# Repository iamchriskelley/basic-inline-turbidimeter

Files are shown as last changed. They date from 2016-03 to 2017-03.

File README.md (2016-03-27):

#Basic Inline Turbidimeter
##Purpose  
The Basic Inline Turbidimeter is designed to measure turbidity in a body of water, automatically, for the lowest possible price.  

##Function  
_How does the device measure a parameter?_  
This device is a back-scatter [nephelometrer](https://en.wikipedia.org/wiki/Nephelometer). A pair of infrared light-emitting diodes (IR LED) are mounted on either side of a light-to-frequency sensor. Some portion of this emitted light is scattered by suspended sediment as it passes through a sample of water. This scattered light is detected by an IR-sensitive [photodiode](https://en.wikipedia.org/wiki/Photodiode) mounted at a right angle to the center of the IR LED's light beam. The intensity of light detected by the photodiode is referenced to a calibration curve stored in the device's memory to interpolate the corresponding turbidity value, measured in [nephelometric turbidity units (NTU)](http://or.water.usgs.gov/grapher/fnu.html).  

_How does the device record data?_  
This device contains an SD card slot for storing data.   

_How does the device display data?_  
This device is intended for standalone data logging and does not include a display.  

_What units does the device report in?_  
Like all AWQUA turbidimeters, this device reports readings in  [nephelometric turbidity units (NTU)](http://or.water.usgs.gov/grapher/fnu.html).  

_How does the device communicate data electronically?_  
This device does not possess data telemetry capabilities, however they may be added for additional cost. See the [Communications](https://github.com/AWQUA/Communication) repo for options. 

##Use Case  
_Where can the device be safely used?_  
This device can handle temperatures up to 70C, and is intended for field conditions. It is water proof to at least one foot.

##Power  
_How is the device powered?_  
This device uses 3.3V DC power, and requires less than 100mA of current, and uses an internal 3.7V lithium polymer battery.

_How much power does it use?_  
In automated testing, this device was capable of taking a measurement every 15 minutes for 29.5 days.

##Standard and Testing  
_How was the device tested?_  
This device has so far only been tested in the Open Source Water lab. The testing consisted of:
(1) immersing a prototype device in a water bath which contains a spin plate for bath mixing  
(2) adding small doses of a colloidal suspension to the water bath while relaying readings from the prototype via Bluetooth  every 10 seconds
(3) on every fourth dose of colloidal suspension, sampling the water bath with a commercial handheld turbidimeter  
(4) analyzing the fit between the commercial and prototype open-source turbidimeter

_How did it perform?_  
Test results may be found in the `testing` subdirectory in the file `basic-inline-turbidimeter_analysis.20151021.xlsx`. These data will be updated as further testing is conducted.

_What performance standards does the device meet?_  
We have not evaluated this device against existing standards for backscatter turbidimeters yet, nor have we yet developed a new standard.

##Construction  

###Bill of Materials
| Quantity  | Part Description | Example Price (each) |
| :-------------: | ------------- | :-------------: |
| 1 | ATMega328P-PU microprocessor  | [$2.90](http://www.electrodragon.com/product/atmega328-with-arduino-optiboot-uno/)|
| 1 | LMT86 temperature sensor  | [$1.00](http://www.mouser.com/ProductDetail/Texas-Instruments/LMT86LP/?qs=sGAEpiMZZMvfFCidbTccA1jyVRrxk5nB%252bTEjPRynSGM%3d)|
| 1 | TSL230BRD  | [$5.03](http://www.mouser.com/ProductDetail/ams/TSL230BRD-TR/?qs=sGAEpiMZZMu97qiQi8P%252buifvOPr%252b402N67DKHn09PFo%3d)|
| 1 | LP2985 3.3V Voltage regulator  | [$1.04](http://www.mouser.com/ProductDetail/Texas-Instruments/LP2985-33DBVT/?qs=paYhMW8qfivCywxvLCGbYQ%3D%3D)|
| 2 | 10uF aluminum electrolytic capacitors  | [$0.24](http://www.mouser.com/ProductDetail/Nichicon/ULD1J100MDD1TD/?qs=sGAEpiMZZMvwFf0viD3Y3c1N%2fF%2fpDmX12XlNW9X9Y3vZmYyMo5GpOw%3d%3d)|
| 2 | 22pF ceramic capacitors  | [$0.03](http://www.mouser.com/ProductDetail/Vishay-BC-Components/K220J10C0GF5UH5/?qs=sGAEpiMZZMsh%252b1woXyUXj9nJp%252b8gphztXIKBUu3gv%252bs%3d)|
| 5 | 100nF ceramic capacitors  | [$0.06](http://www.mouser.com/ProductDetail/Vishay-BC-Components/K104Z15Y5VE5TL2/?qs=sGAEpiMZZMsh%252b1woXyUXj5VNmf0jXPWIrWjnp1zAXac%3d)|
| 4 | 100 ohm resistors  | [$0.10](http://www.mouser.com/ProductDetail/KOA-Speer/MOS1-2CT52R101J/?qs=sGAEpiMZZMtlubZbdhIBICYVxaT5CDYBpEIIN%2f0BoAk%3d)|
| 1 | 220 ohm resistors  | [$0.10](http://www.mouser.com/ProductDetail/KOA-Speer/MOS1-2CT52R221J/?qs=sGAEpiMZZMtlubZbdhIBICYVxaT5CDYBStqm8FrIljg%3d)|
| 1 | 1K ohm resistors 1% tolerance | [$0.10](http://www.mouser.com/ProductDetail/Vishay-Beyschlag/MBB02070C1001FCT00/?qs=sGAEpiMZZMtlubZbdhIBIAA6NYEPHyksoxlYyK2s%252btM%3d)|
| 4 | 10K ohm resistors  | [$0.10](http://www.mouser.com/ProductDetail/Vishay-Beyschlag/MBA02040C1002FCT00/?qs=sGAEpiMZZMtlubZbdhIBIP7908E9uONJr6Tgqqo7oLA%3d)|
| 1 | IR LED  | [$0.47](http://www.mouser.com/ProductDetail/Kingbright/WP7113SF4C/?qs=sGAEpiMZZMvAL21a%2fDhxMro1KOf4QOs%252bCw5JRgjZK8o%3d)|
| 1 | Momentary contact button  | [$1.50](http://www.mouser.com/)|
| 1 | SPST power switch  | [$1.50](http://www.mouser.com/)|
| x | Header pins (0.1" spacing)  | [$1.50](http://www.mouser.com/)|
|||
||Total Cost:|$xx.xx|
###Circuit Board
####Schematic
picture alt Schematic of Basic Handheld Turbidimeter circuit board
####Layout
picture alt Layout of Basic Handheld Turbidimeter circuit board
###Assembly
[forthcoming]  
##FAQ and Troubleshooting  
###Online Resources

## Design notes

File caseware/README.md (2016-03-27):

#Caseware
The case for the `basic-inline-turbidimeter` is an injection-moded plastic case in two halves, manufactured by [SERPAC](http://www.serpac.com/). This case measures 2.27 x 3.63 x 1.51 inches and -- with the addition of a matching rubber seal between the two case halves -- is waterproof. Example pricing information below.

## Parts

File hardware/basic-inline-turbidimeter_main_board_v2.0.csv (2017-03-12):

Part | Value | Device | Package | Description | MF | MPN | OC_FARNELL | OC_NEWARK | PROD_ID
*RTC |  | DS3231M | DS3231M
C1 | 18p | CAP0603-CAP | 0603-CAP | Capacitor
C2 | 18p | CAP0603-CAP | 0603-CAP | Capacitor
C4 | 100n | CAP0603-CAP | 0603-CAP | Capacitor
C5 | 100n | CAP0603-CAP | 0603-CAP | Capacitor
C6 | 100n | CAP0603-CAP | 0603-CAP | Capacitor
C7 | 100n | CAP0603-CAP | 0603-CAP | Capacitor
C8 | 100n | CAP0603-CAP | 0603-CAP | Capacitor
C12 | 10uF | CAP0603-CAP | 0603-CAP | Capacitor
IC1 | MEGA8-AI | MEGA8-AI | TQFP32-08 | MICROCONTROLLER |  | ATMEGA8-16AU | 9171371 | 73M8863
JP1 |  | M02PTH | 1X02 | Standard 2-pin 0.1 header. Use with"
JP2 |  | M01PTH | 1X01 | Header 1
JP5 |  | M06SILK_FEMALE_PTH | 1X06 | Header 6 |  |  |  |  | CONN-08437
JP6 |  | M06SILK_FEMALE_PTH | 1X06 | Header 6 |  |  |  |  | CONN-08437
JP8 |  | M07 | 1X07 | Header 7
MICRO-SD | MICROSD-1010030368 | MICROSD-1010030368 | MICROSD-1010030368
PAD1 | WIREPADSMD5-2,5 | WIREPADSMD5-2,5 | 5-2,5 | Wire PAD connect wire on PCB
PAD2 | WIREPADSMD5-2,5 | WIREPADSMD5-2,5 | 5-2,5 | Wire PAD connect wire on PCB
PAD3 | WIREPADSMD5-2,5 | WIREPADSMD5-2,5 | 5-2,5 | Wire PAD connect wire on PCB
PAD4 | WIREPADSMD5-2,5 | WIREPADSMD5-2,5 | 5-2,5 | Wire PAD connect wire on PCB
R1 | 10k | RESISTOR0603 | 0603-RES | Resistor
R2 | 1k | RESISTOR0603 | 0603-RES | Resistor
U$4 | LMT86 | LMT86 | LMT86
Y1 |  | CRYSTAL5X3 | CRYSTAL-SMD-5X3 | Crystals

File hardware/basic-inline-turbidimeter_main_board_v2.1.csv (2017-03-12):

Part | Value | Device | Package | Description
BT |  | M04PTH | 1X04 | Header 4
C1 | 18p | CAP0603-CAP | 0603-CAP | Capacitor
C2 | 18p | CAP0603-CAP | 0603-CAP | Capacitor
C3 | 10uF | CAP0603-CAP | 0603-CAP | Capacitor
C4 | 100n | CAP0603-CAP | 0603-CAP | Capacitor
C5 | 100n | CAP0603-CAP | 0603-CAP | Capacitor
C6 | 100n | CAP0603-CAP | 0603-CAP | Capacitor
C7 | OPT | CAP0603-CAP | 0603-CAP | Capacitor
C8 | 100n | CAP0603-CAP | 0603-CAP | Capacitor
C9 | 100n | CAP0603-CAP | 0603-CAP | Capacitor
C10 | 100n | CAP0603-CAP | 0603-CAP | Capacitor
C11 | 100n | CAP0603-CAP | 0603-CAP | Capacitor
C12 | 100n | CAP0603-CAP | 0603-CAP | Capacitor
FRAME1 | FRAME-LETTER | FRAME-LETTER | CREATIVE_COMMONS | Schematic Frame
IC1 | MEGA8-AI | MEGA8-AI | TQFP32-08 | MICROCONTROLLER
IC2 | LM358 | LM358D | SO08 | OP AMP also LM158; LM258; LM2904
IND |  | M02PTH | 1X02 | Standard 2-pin 0.1 header. Use with"
ISP | AVR_SPI_PRG_6PTH | AVR_SPI_PRG_6PTH | 2X3 | AVR ISP 6 Pin
JP1 |  | M01PTH | 1X01 | Header 1
LED1 |  | LED5MM | LED5MM | LEDs
LED2 |  | LED5MM | LED5MM | LEDs
LED3 |  | LED5MM | LED5MM | LEDs
LED4 |  | LED5MM | LED5MM | LEDs
ND |  | M01PTH | 1X01 | Header 1
PW |  | M01PTH | 1X01 | Header 1
PWR |  | M03PTH | 1X03 | Header 3
R1 | 32k | RESISTOR0603 | 0603-RES | Resistor
R2 | 10k | RESISTOR0603 | 0603-RES | Resistor
R3 | 10k | RESISTOR0603 | 0603-RES | Resistor
R4 | 10k | RESISTOR0603 | 0603-RES | Resistor
R5 | 10k | RESISTOR0603 | 0603-RES | Resistor
R6 | 22 | RESISTOR0603 | 0603-RES | Resistor
R7 | 10k | RESISTOR0603 | 0603-RES | Resistor
R8 | OPT | RESISTOR0603 | 0603-RES | Resistor
R13 | 10k | RESISTOR0603 | 0603-RES | Resistor
R14 | 10k | RESISTOR0603 | 0603-RES | Resistor
R16 | 10k_<1% | RESISTOR0603-RES | 0603-RES | Resistor
RD |  | M01PTH | 1X01 | Header 1
REED |  | M02PTH | 1X02 | Standard 2-pin 0.1 header. Use with"
RT |  | M01PTH | 1X01 | Header 1
RTC |  | M04PTH | 1X04 | Header 4
SJ1 | JUMPER-PAD-2-NOYES_SILK | JUMPER-PAD-2-NOYES_SILK | PAD-JUMPER-2-NO_YES_SILK
SJ2 | JUMPER-PAD-2-NOYES_SILK | JUMPER-PAD-2-NOYES_SILK | PAD-JUMPER-2-NO_YES_SILK
T1 | 2N2222 | 2N2222 | TO92-EBC-OVAL | NPN TRANSISTOR
T2 | 2N2222 | 2N2222 | TO92-EBC-OVAL | NPN TRANSISTOR
THERM |  | RESISTOR0603-RES | 0603-RES | Resistor
TP |  | M01PTH | 1X01 | Header 1
TSL267 |  | M03PTH | 1X03 | Header 3
U1 | EEPROM-I2CSMD | EEPROM-I2CSMD | SO08 | I2C EEPROM chips, 24LC256 (and others)
U2 | EEPROM-I2CSMD | EEPROM-I2CSMD | SO08 | I2C EEPROM chips, 24LC256 (and others)
U3 | ADS1115 | ADS1115IDGST | SOP50P490X110-10N | Analog-to-Digital Converter with Internal Reference
U4 | MCP9808 | MCP9808-E/MS | SOP65P490X110-8N | Board Mount Temperature Sensors Silicon temp sensor with I2C interface
UART |  | M06SILK_FEMALE_PTH | 1X06 | Header 6
Y1 |  | CRYSTAL5X3 | CRYSTAL-SMD-5X3 | Crystals

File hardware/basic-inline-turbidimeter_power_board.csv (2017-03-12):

Part | Value | Device | Package | Description | PROD_ID
+OUT- |  | M02PTH | 1X02 | Standard 2-pin 0.1 header. Use with"
1UF |  | CAP0603-CAP | 0603-CAP | Capacitor
2.2UF |  | CAP0603-CAP | 0603-CAP | Capacitor
C3 | 4.7uF | CAP0402-CAP | 0402-CAP | Capacitor
C4 | 4.7uF | CAP0402-CAP | 0402-CAP | Capacitor
D1 | GREEN | LED0603 | LED-0603 | LEDs
D2 | MBRA140 | MBRA140 | SMA-DIODE | 40V, 1A Schottky rectifier | DIO-08053
D11 | RED | LED0603 | LED-0603 | LEDs
JMP |  | M02PTH | 1X02 | Header 2
JP2 |  | M02PTH | 1X02 | Standard 2-pin 0.1 header. Use with"
JP7 | LiPo Battery | M02-JST-2MM-SMT | JST-2-SMD | Header 2
OPT_10NF |  | CAP0603-CAP | 0603-CAP | Capacitor
R1 | R330 | RESISTOR0402-RES | 0402-RES | Resistor
R2K | 2K | RESISTOR0402-RES | 0402-RES | Resistor
R330 | 330 | RESISTOR0402-RES | 0402-RES | Resistor
U$2 | LP2985 | LP2985 | LP2985
U1 | MCP73831 | MCP73831 | SOT23-5 | Microchip's MCP73831

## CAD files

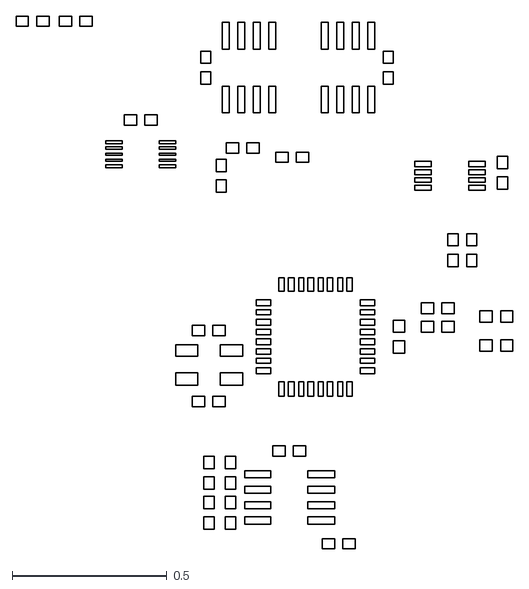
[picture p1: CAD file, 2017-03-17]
hardware/basic-inline-turbidimeter_main_board_v2.1.dxf
1.61 x 1.72

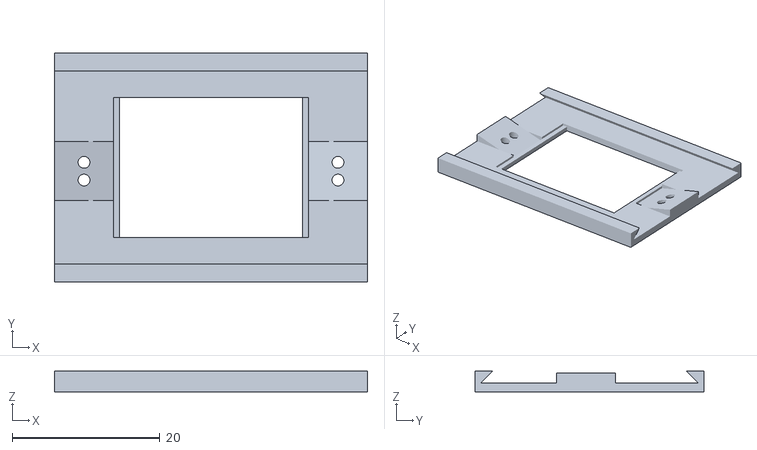
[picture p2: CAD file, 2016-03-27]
caseware/inline-light-angler.stl
42.4 x 31.0 x 2.80

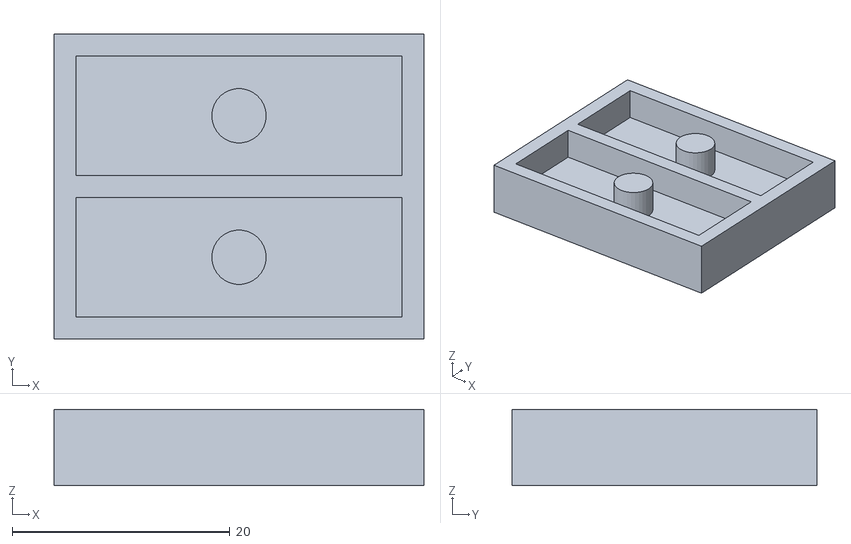
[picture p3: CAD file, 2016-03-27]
caseware/inline-cable-gaskets.stl
34.0 x 28.0 x 7.00

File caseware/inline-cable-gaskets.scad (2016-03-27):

$fn=30;
difference(){
    cube([34,28,7]);
    translate([2,2,3]) difference(){
        cube([30,11,4]);
        translate([15,5.5,0]) cylinder(r=2.5, h=4);
    }
    translate([2,15,3]) difference(){
        cube([30,11,4]);
        translate([15,5.5,0]) cylinder(r=2.5, h=4);
    }
}

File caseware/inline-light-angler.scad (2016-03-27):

$fn=30;

//translate([4,13,4]) rotate([0,-90,0]) 
light_shield();


module prism(hgt,sz){
rotate([0,0,0]) linear_extrude(height=hgt, center=true)
polygon(points = [ [0,0], [0,sz], [sz,sz]], paths = [ [0, 1, 2]]);
}

module light_shield(){
lightback();
translate([34.4,0,0]) rotate([0,0,180]) lightback();
translate([-4,10,0]) cube([42.4,6,1.2]);
translate([-4,-15,0]) cube([42.4,6,1.2]);
translate([-4,-15,0]) cube([42.4,6,1.2]);
translate([17.2,13.6,2.8]) rotate([0,90,0]) prism(42.4,2.4);
translate([17.2,-15,0.4]) rotate([90,0,90]) prism(42.4,2.4);
}

module lightback(){
    union(){
        difference(){
            //cylinder(r=4, h=2);
            translate([-4,-4,0]) cube([8,8,3]);
            //translate([-1,0,1.6]) rotate([0,15,0]) cylinder(r=10, h=3);
            translate([0,0,3]) rotate([0,15,0]) cube([18,18,3], true);
            translate([0,1.2,0])  cylinder(r=.8, h=3);
            translate([0,-1.2,0])  cylinder(r=.8, h=3);
        }
        translate([-4,4,0]) cube([8,6,1.2]);
        translate([-4,-10,0]) cube([8,6,1.2]);
        translate([4,-10,0]) cube([.8,20,.8]);
    }
}

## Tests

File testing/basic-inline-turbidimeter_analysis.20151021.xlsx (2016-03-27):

writing to logfile | 574 | 3.29 | 2015-10-21 16:07 | 1050.667
writing to logfile | 574.06 | 3.29 | 2015-10-21 16:07 | 1156.333
writing to logfile | 573.81 | 3.29 | 2015-10-21 16:07 | 1157.5
writing to logfile | 574 | 3.29 | 2015-10-21 16:08 | 1158.5
writing to logfile | 573.56 | 3.3 | 2015-10-21 16:08 | 1159.667
writing to logfile | 573.5 | 3.29 | 2015-10-21 16:08 | 1160.667
writing to logfile | 573.31 | 3.29 | 2015-10-21 16:08 | 1158
writing to logfile | 573.19 | 3.3 | 2015-10-21 16:08 | 1158
writing to logfile | 573.13 | 3.3 | 2015-10-21 16:08 | 1157.667
writing to logfile | 573.13 | 3.29 | 2015-10-21 16:09 | 1164
writing to logfile | 573.19 | 3.29 | 2015-10-21 16:09 | 1159
writing to logfile | 572.75 | 3.3 | 2015-10-21 16:09 | 1160.833
writing to logfile | 572.94 | 3.29 | 2015-10-21 16:09 | 1159
writing to logfile | 573.06 | 3.29 | 2015-10-21 16:09 | 1157.167
writing to logfile | 572.94 | 3.29 | 2015-10-21 16:09 | 713.667
writing to logfile | 572.81 | 3.3 | 2015-10-21 16:10 | 936.167
writing to logfile | 572.63 | 3.29 | 2015-10-21 16:10 | 911.667
writing to logfile | 572.63 | 3.29 | 2015-10-21 16:10 | 600.167
writing to logfile | 572.31 | 3.29 | 2015-10-21 16:10 | 204
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

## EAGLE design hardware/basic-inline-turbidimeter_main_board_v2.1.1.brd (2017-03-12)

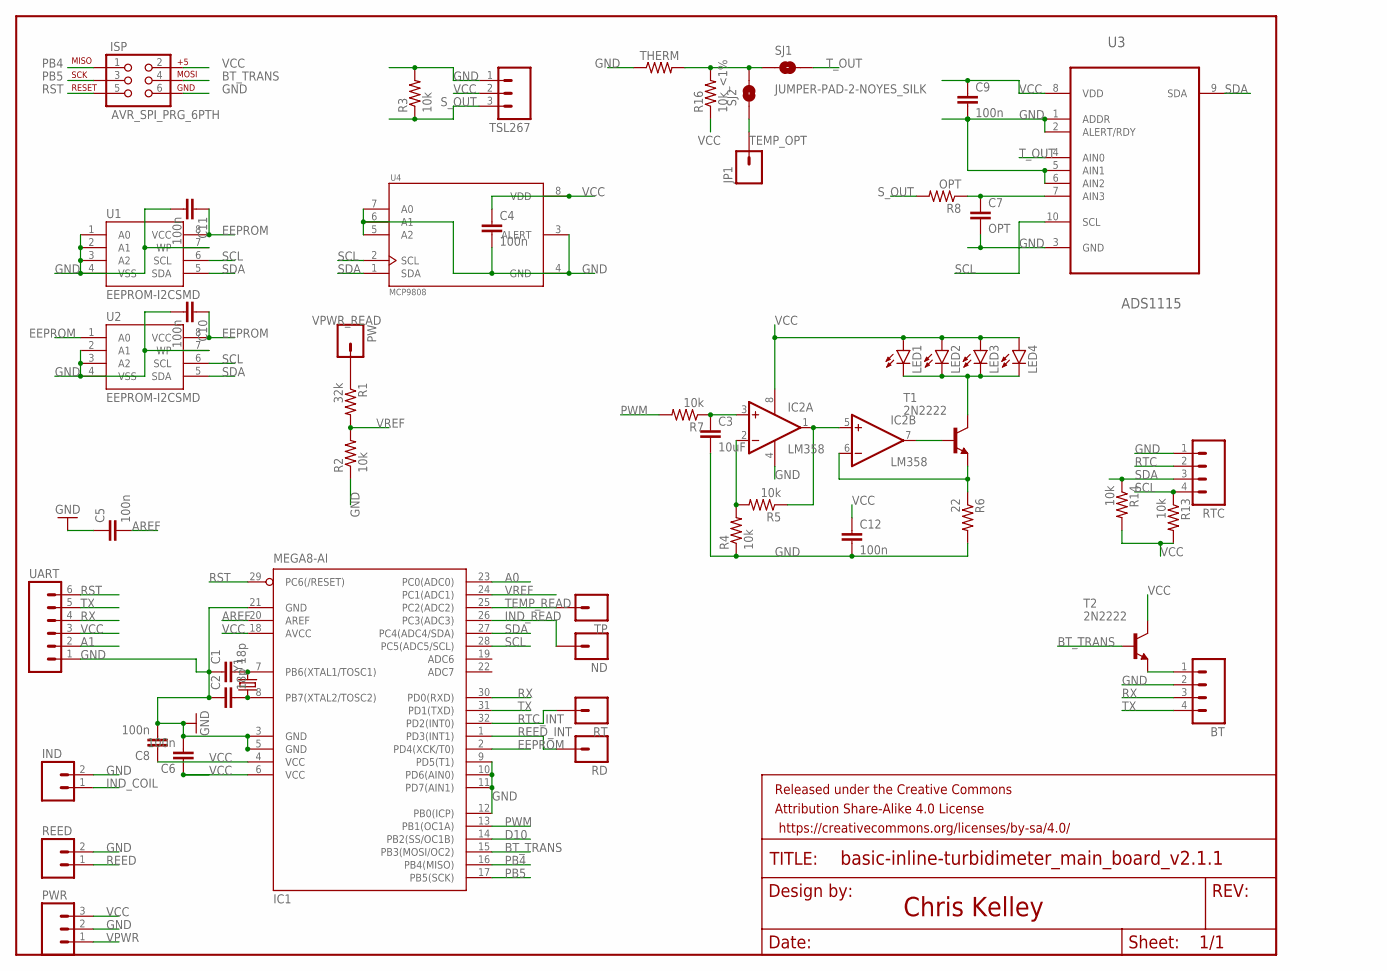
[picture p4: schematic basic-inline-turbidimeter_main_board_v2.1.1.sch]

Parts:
BT: M04PTH; 1X04
C1, C2: 18p; 0603-CAP
C3: 10uF; 0603-CAP
C4, C5, C6, C8, C9, C10, C11, C12: 100n; 0603-CAP
C7: OPT; 0603-CAP
FRAME1: FRAME-LETTER; CREATIVE_COMMONS
IC1: MEGA8-AI; TQFP32-08
IC2: LM358; SO08
IND: M02PTH; 1X02
ISP: AVR_SPI_PRG_6PTH; 2X3
JP1: M01PTH; 1X01
LED1, LED2, LED3, LED4: LED5MM
ND: M01PTH; 1X01
PW: M01PTH; 1X01
PWR: M03PTH; 1X03
R1: 32k; 0603-RES
R2, R3, R4, R5, R7, R13, R14: 10k; 0603-RES
R6: 22; 0603-RES
R8: OPT; 0603-RES
R16: 10k_<1%; 0603-RES
RD: M01PTH; 1X01
REED: M02PTH; 1X02
RT: M01PTH; 1X01
RTC: M04PTH; 1X04
SJ1, SJ2: JUMPER-PAD-2-NOYES_SILK; PAD-JUMPER-2-NO_YES_SILK
T1, T2: 2N2222; TO92-EBC-OVAL
THERM: RESISTOR0603-RES; 0603-RES
TP: M01PTH; 1X01
TSL267: M03PTH; 1X03
U1, U2: EEPROM-I2CSMD; SO08
U3: ADS1115; SOP50P490X110-10N
U4: MCP9808; SOP65P490X110-8N
UART: M06SILK_FEMALE_PTH; 1X06
Y1: CRYSTAL5X3; CRYSTAL-SMD-5X3

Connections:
A0: IC1.23 (PC0(ADC0))
A1: UART.2
AREF: C5.2, IC1.20 (AREF)
BT_TRANS: IC1.15 (PB3(MOSI/OC2)), ISP.4, T2.B
D10: IC1.14 (PB2(SS/OC1B))
EEPROM: C10.1, C11.1, IC1.2 (PD4(XCK/T0)), U1.8 (VCC), U2.1 (A0), U2.8 (VCC)
GND: BT.2, C1.1, C2.1, C3.2, C4.2, C5.1, C6.2, C7.2, C8.2, C9.2, C10.2, C11.2, C12.2, IC1.3 (GND), IC1.5 (GND), IC1.9 (PD5(T1)), IC1.10 (PD6(AIN0)), IC1.11 (PD7(AIN1)), IC1.12 (PB0(ICP)), IC1.21 (GND), IC2.4 (V-), IND.2, ISP.6, PWR.2, R2.1, R3.2, R4.1, R6.2, REED.2, RTC.1, THERM.1, TSL267.1, U1.1 (A0), U1.2 (A1), U1.3 (A2), U1.4 (VSS), U1.7 (WP), U2.2 (A1), U2.3 (A2), U2.4 (VSS), U2.7 (WP), U3.1 (ADDR), U3.2 (ALERT/RDY), U3.3 (GND), U3.5 (AIN1), U3.6 (AIN2), U4.3 (ALERT), U4.4 (GND), U4.5 (A2), U4.6 (A1), U4.7 (A0), UART.1
IND_COIL: IND.1
IND_READ: IC1.26 (PC3(ADC3)), ND.1
unnamed: LED1.K (C), LED2.K (C), LED3.K (C), LED4.K (C), T1.C
unnamed: C7.1, R8.1, U3.7 (AIN3)
unnamed: C3.1, IC2.3 (+IN), R7.1
unnamed: IC2.1 (OUT), IC2.5 (+IN), R5.1
unnamed: IC2.7 (OUT), T1.B
unnamed: IC2.2 (-IN), R4.2, R5.2
unnamed: IC2.6 (-IN), R6.1, T1.E
unnamed: BT.1, T2.E
unnamed: R16.2, SJ1.1, SJ2.2, THERM.2
PB4: IC1.16 (PB4(MISO)), ISP.1
PB5: IC1.17 (PB5(SCK)), ISP.3
PWM: IC1.13 (PB1(OC1A)), R7.2
Q1: C2.2, IC1.8 (PB7(XTAL2/TOSC2)), Y1.1
Q2: C1.2, IC1.7 (PB6(XTAL1/TOSC1)), Y1.3 (2)
REED: REED.1
REED_INT: IC1.1 (PD3(INT1)), RD.1
RST: IC1.29 (PC6(/RESET)), ISP.5, UART.6
RTC: RTC.2
RTC_INT: IC1.32 (PD2(INT0)), RT.1
RX: BT.3, IC1.30 (PD0(RXD)), UART.4
SCL: IC1.28 (PC5(ADC5/SCL)), R13.1, RTC.4, U1.6 (SCL), U2.6 (SCL), U3.10 (SCL), U4.2 (SCL)
SDA: IC1.27 (PC4(ADC4/SDA)), R14.1, RTC.3, U1.5 (SDA), U2.5 (SDA), U3.9 (SDA), U4.1 (SDA)
S_OUT: R3.1, R8.2, TSL267.3
TEMP_OPT: JP1.1, SJ2.1
TEMP_READ: IC1.25 (PC2(ADC2)), TP.1
TX: BT.4, IC1.31 (PD1(TXD)), UART.5
T_OUT: SJ1.2, U3.4 (AIN0)
VCC: C4.1, C6.1, C8.1, C9.1, C12.1, IC1.4 (VCC), IC1.6 (VCC), IC1.18 (AVCC), IC2.8 (V+), ISP.2, LED1.A, LED2.A, LED3.A, LED4.A, PWR.3, R13.2, R14.2, R16.1, T2.C, TSL267.2, U3.8 (VDD), U4.8 (VDD), UART.3
VPWR: PWR.1
VPWR_READ: PW.1, R1.1
VREF: IC1.24 (PC1(ADC1)), R1.2, R2.2

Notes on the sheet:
Chris Kelley

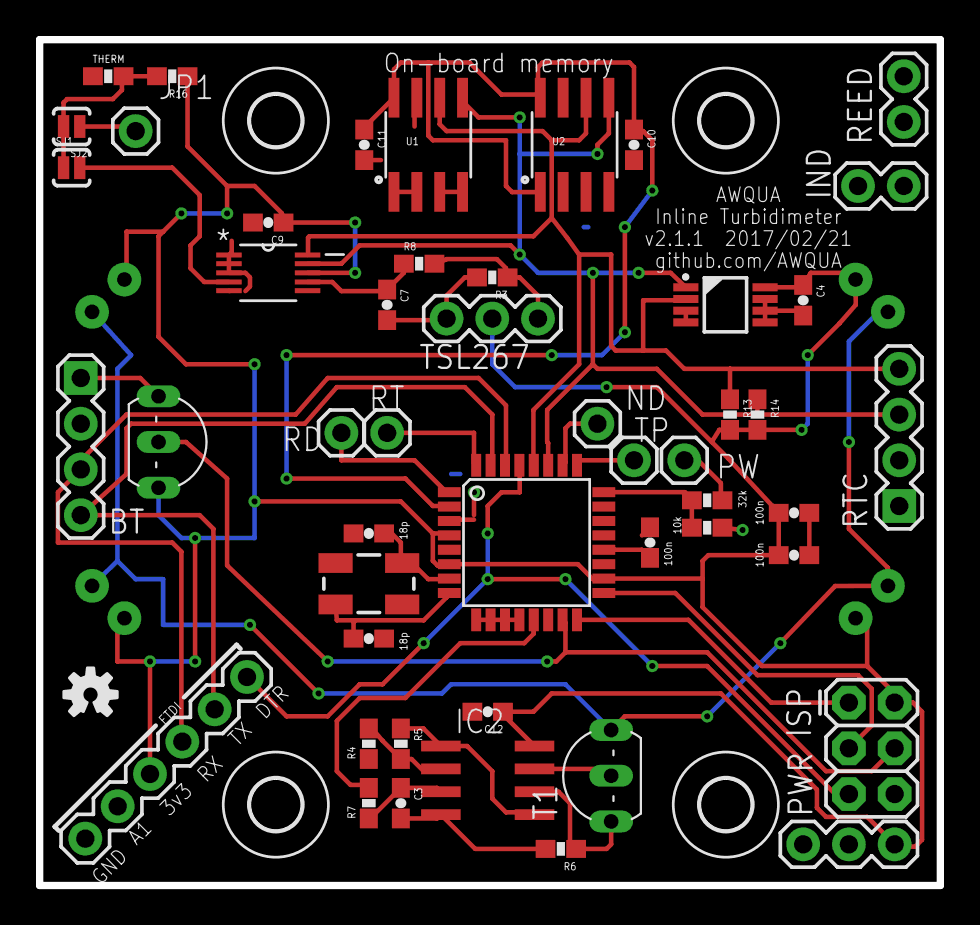
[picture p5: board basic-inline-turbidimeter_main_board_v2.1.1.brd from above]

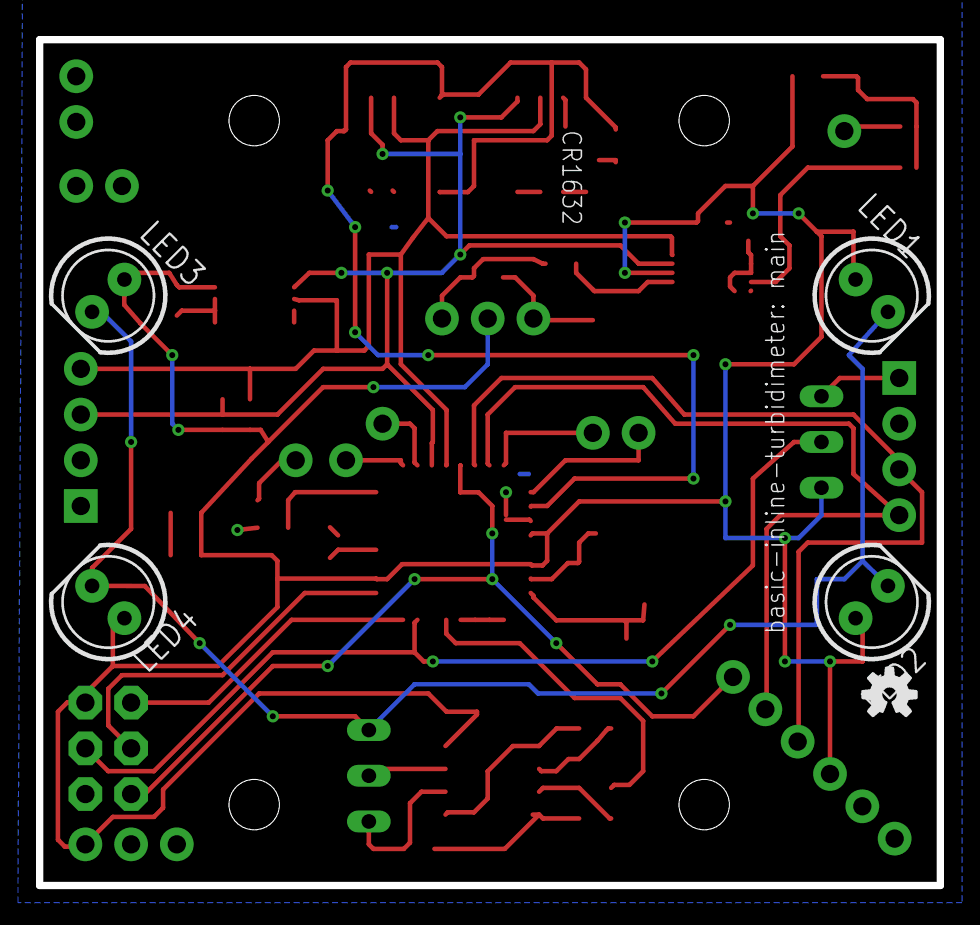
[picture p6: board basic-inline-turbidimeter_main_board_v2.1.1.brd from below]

Board: 2 copper layers, 50.0 x 47.0 mm, 60 parts (5 on the bottom side), 33 nets.

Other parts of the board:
U$1, U$3, U$5, U$6: 2,8
U$2, U$8: OSHW-LOGO-S

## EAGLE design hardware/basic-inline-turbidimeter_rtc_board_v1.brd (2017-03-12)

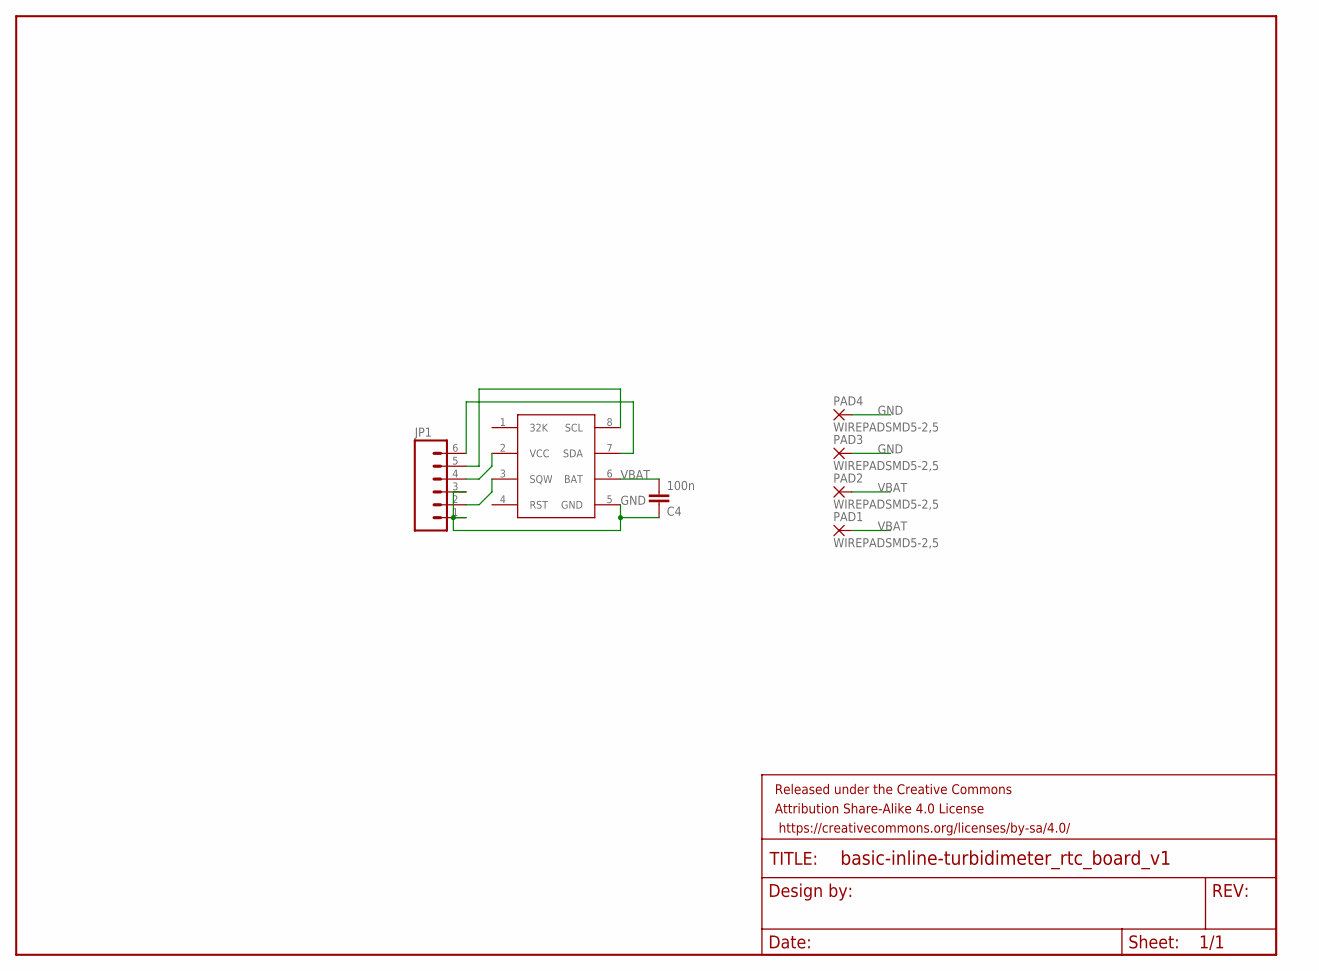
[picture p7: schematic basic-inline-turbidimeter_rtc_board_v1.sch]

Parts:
*RTC: DS3231M
C4: 100n; 0603-CAP
FRAME1: FRAME-LETTER; CREATIVE_COMMONS
JP1: M06SILK_FEMALE_PTH; 1X06
PAD1, PAD2, PAD3, PAD4: WIREPADSMD5-2,5; 5-2,5

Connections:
GND: *RTC.5 (GND), C4.1, JP1.1, JP1.3, PAD3.1, PAD4.1
unnamed: *RTC.3 (SQW), JP1.2
SCL: *RTC.8 (SCL), JP1.5
SDA: *RTC.7 (SDA), JP1.6
VBAT: *RTC.6 (BAT), C4.2, PAD1.1, PAD2.1
VCC: *RTC.2 (VCC), JP1.4

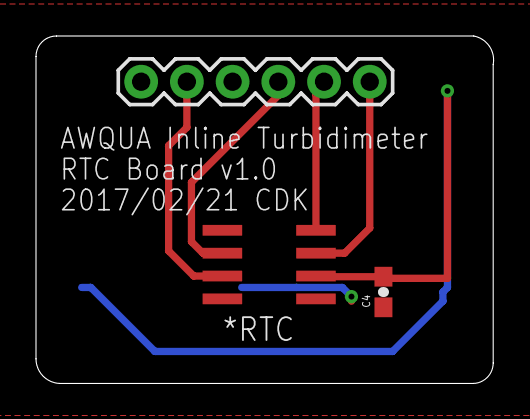
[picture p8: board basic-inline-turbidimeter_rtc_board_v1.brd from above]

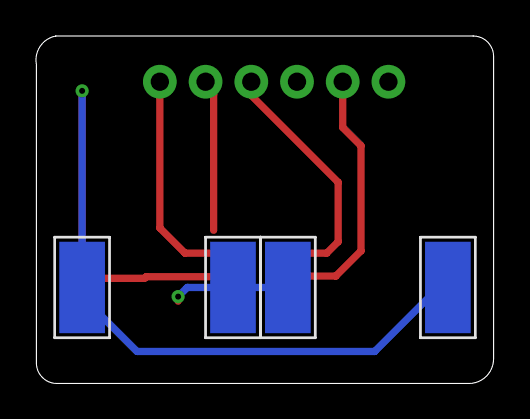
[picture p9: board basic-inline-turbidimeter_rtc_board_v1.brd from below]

Board: 2 copper layers, 25.4 x 19.3 mm, 8 parts (4 on the bottom side), 6 nets.

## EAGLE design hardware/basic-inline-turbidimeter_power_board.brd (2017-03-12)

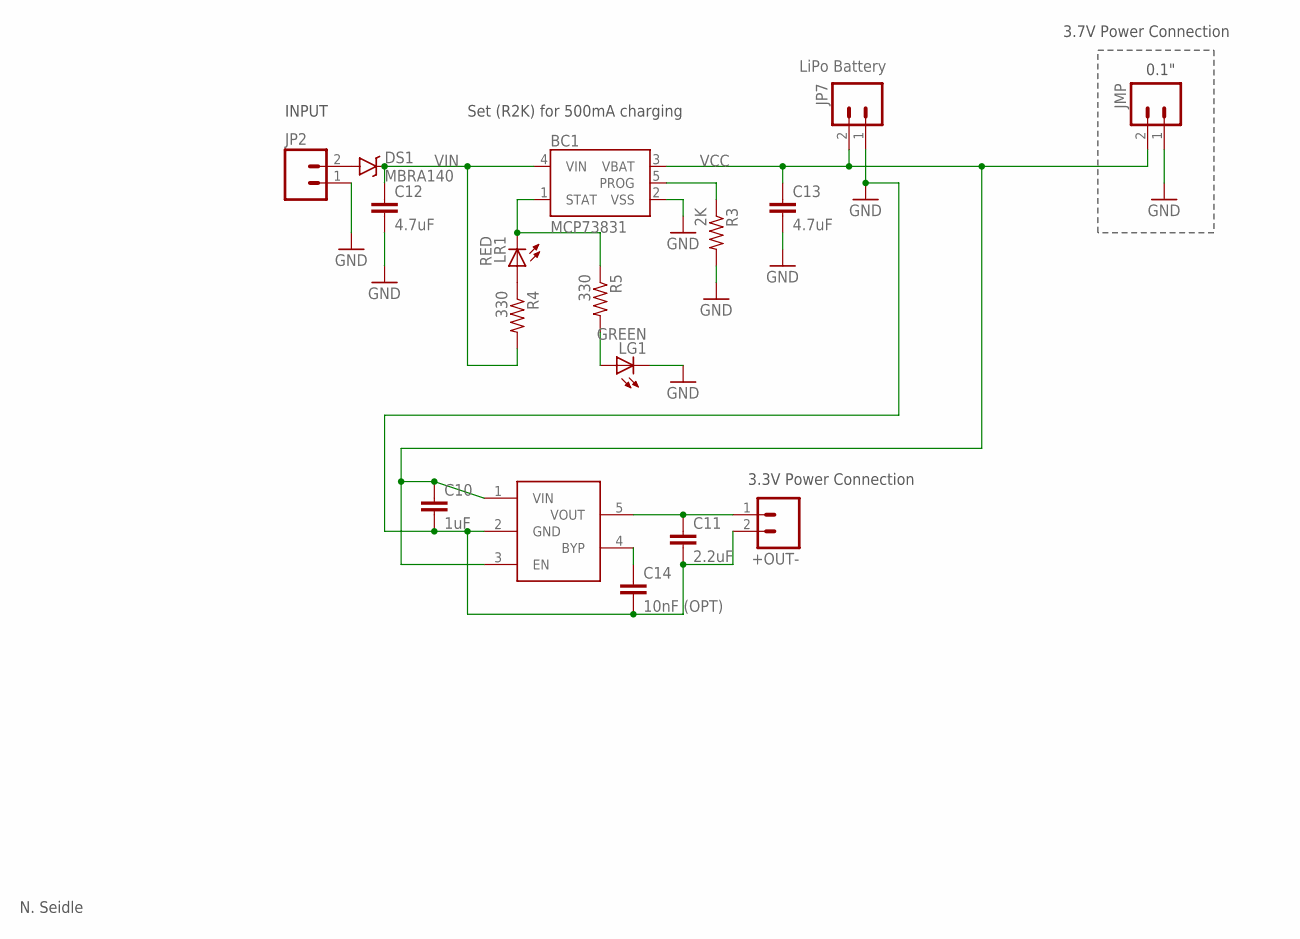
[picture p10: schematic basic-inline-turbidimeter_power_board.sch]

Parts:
+OUT-: M02PTH; 1X02
BC1: MCP73831; SOT23-5
C10: 1uF; 0603-CAP
C11: 2.2uF; 0603-CAP
C12, C13: 4.7uF; 0402-CAP
C14: 10nF (OPT); 0603-CAP
DS1: MBRA140; SMA-DIODE
JMP: M02PTH; 1X02
JP2: M02PTH; 1X02
JP7: LiPo Battery; JST-2-SMD
LG1: GREEN; LED-0603
LR1: RED; LED-0603
R3: 2K; 0402-RES
R4, R5: 330; 0402-RES
VR1: LP2985

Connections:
GND: +OUT-.2, BC1.2 (VSS), C10.2, C11.2, C12.2, C13.2, C14.2, JMP.1, JP2.1, JP7.1, LG1.C, R3.2, VR1.2 (GND)
unnamed: C14.1, VR1.4 (BYP)
unnamed: LG1.A, R5.2
unnamed: LR1.A, R4.1
unnamed: +OUT-.1, C11.1, VR1.5 (VOUT)
unnamed: DS1.A, JP2.2
PROG: BC1.5 (PROG), R3.1
STAT: BC1.1 (STAT), LR1.C, R5.1
VCC: BC1.3 (VBAT), C10.1, C13.1, JMP.2, JP7.2, VR1.1 (VIN), VR1.3 (EN)
VIN: BC1.4 (VIN), C12.1, DS1.C, R4.2

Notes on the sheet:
3.7V Power Connection
0.1"
N. Seidle
3.3V Power Connection
Set (R2K) for 500mA charging
INPUT

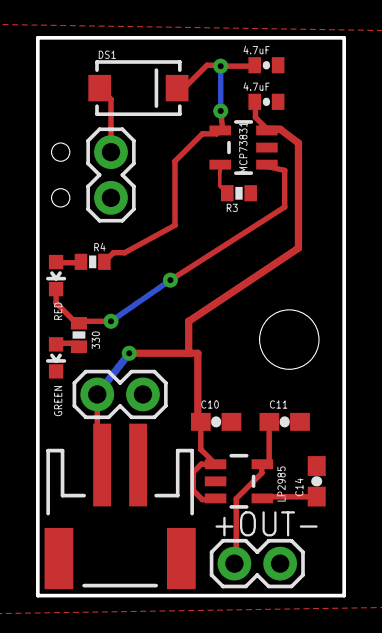
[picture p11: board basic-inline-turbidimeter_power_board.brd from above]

Board: 2 copper layers, 17.0 x 31.0 mm, 18 parts (0 on the bottom side), 10 nets.

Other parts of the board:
JP1: STAND-OFF

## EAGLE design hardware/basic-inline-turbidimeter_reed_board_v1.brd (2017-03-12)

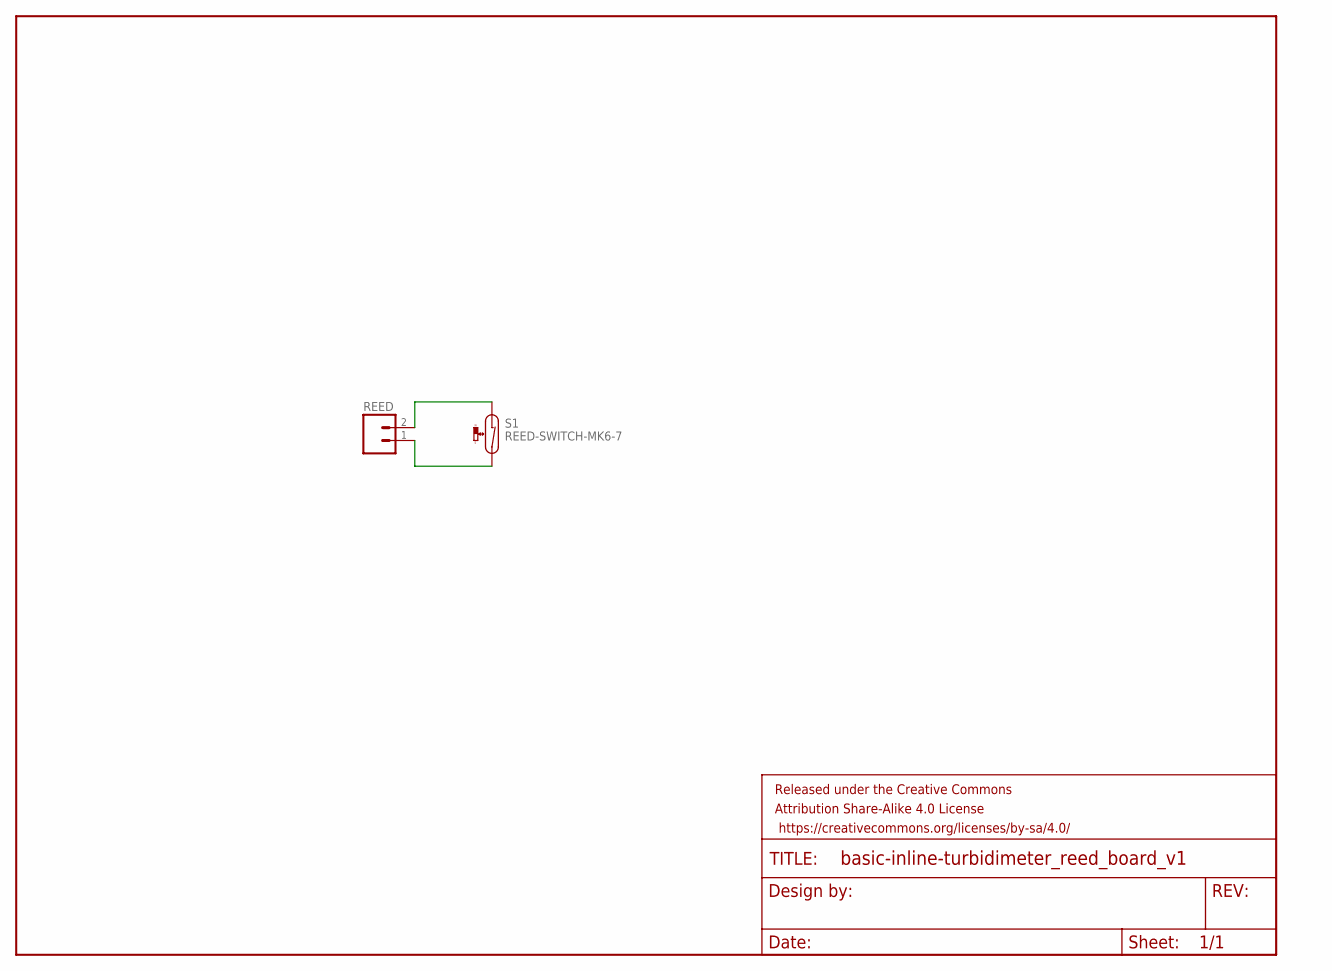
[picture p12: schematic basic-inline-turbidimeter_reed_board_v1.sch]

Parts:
FRAME1: FRAME-LETTER; CREATIVE_COMMONS
REED: M02PTH; 1X02
S1: REED-SWITCH-MK6-7; MK6-7

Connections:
unnamed: REED.2, S1.1
unnamed: REED.1, S1.2

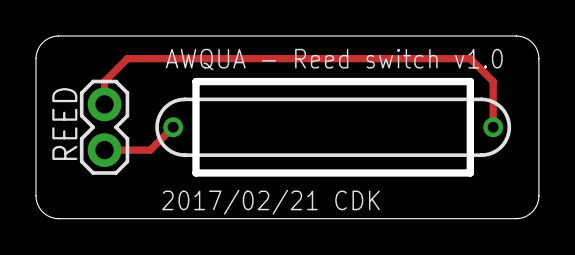
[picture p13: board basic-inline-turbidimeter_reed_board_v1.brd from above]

Board: 2 copper layers, 27.9 x 10.2 mm, 3 parts (0 on the bottom side), 2 nets.

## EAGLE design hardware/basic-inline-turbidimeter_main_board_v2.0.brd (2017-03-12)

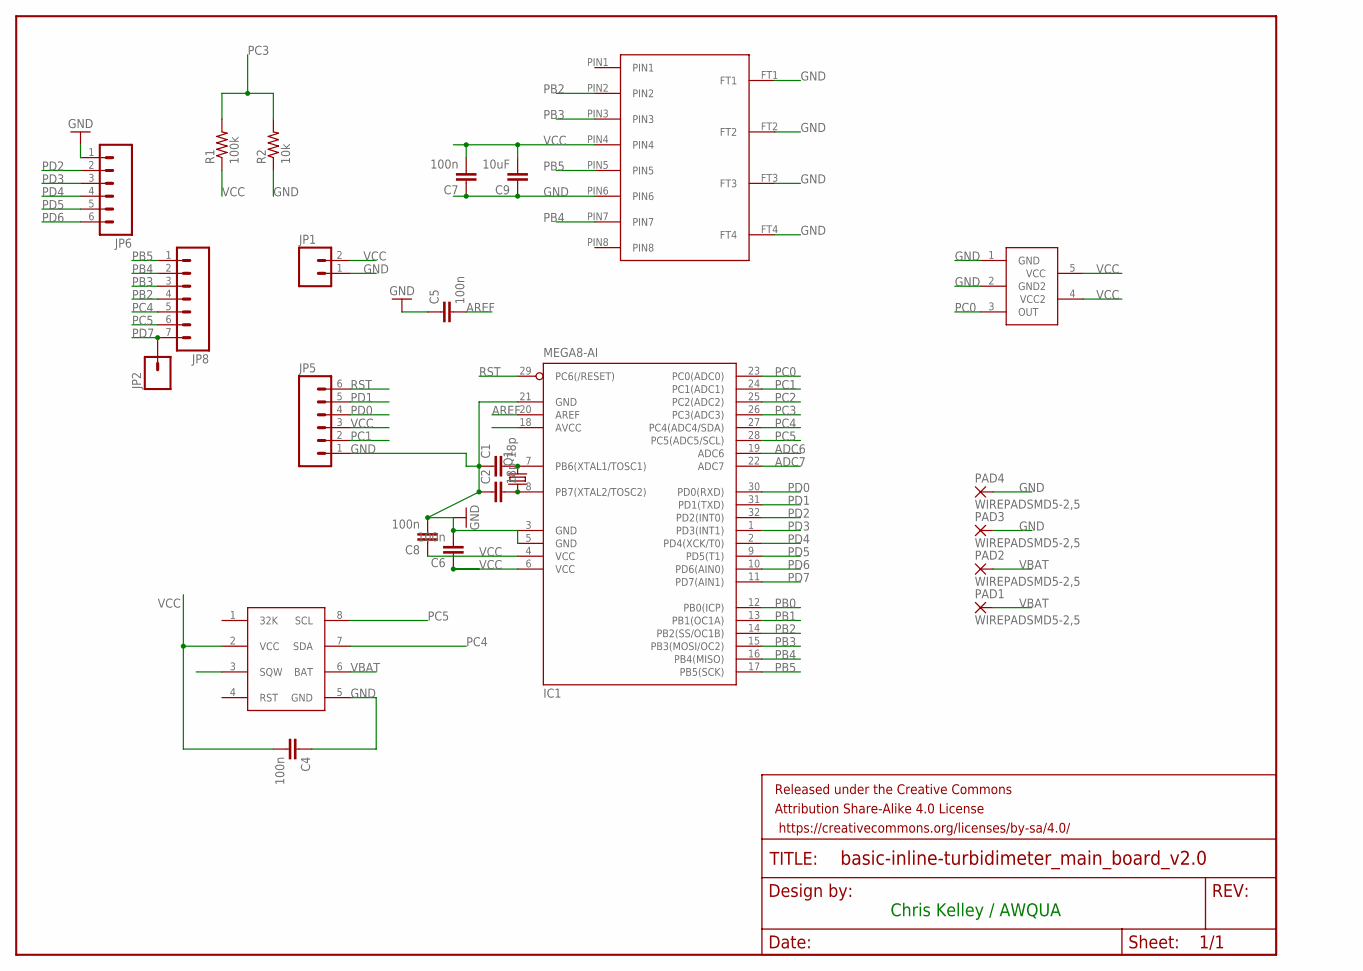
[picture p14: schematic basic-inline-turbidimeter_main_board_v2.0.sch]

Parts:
*RTC: DS3231M
C1, C2: 18p; 0603-CAP
C4, C5, C6, C7, C8: 100n; 0603-CAP
C9: 10uF; 0603-CAP
FRAME1: FRAME-LETTER; CREATIVE_COMMONS
IC1: MEGA8-AI; TQFP32-08
JP1: M02PTH; 1X02
JP2: M01PTH; 1X01
JP5, JP6: M06SILK_FEMALE_PTH; 1X06
JP8: M07; 1X07
MICRO-SD: MICROSD-1010030368
PAD1, PAD2, PAD3, PAD4: WIREPADSMD5-2,5; 5-2,5
Q1: CRYSTAL5X3; CRYSTAL-SMD-5X3
R1: 100k; 0603-RES
R2: 10k; 0603-RES
T1: LMT86

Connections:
ADC6: IC1.19 (ADC6)
ADC7: IC1.22 (ADC7)
AREF: C5.2, IC1.20 (AREF)
GND: *RTC.5 (GND), C1.1, C2.1, C4.1, C5.1, C6.2, C7.1, C8.2, C9.1, IC1.3 (GND), IC1.5 (GND), IC1.21 (GND), JP1.1, JP5.1, JP6.1, MICRO-SD.FT1, MICRO-SD.FT2, MICRO-SD.FT3, MICRO-SD.FT4, MICRO-SD.PIN6, PAD3.1, PAD4.1, R2.1, T1.1 (GND), T1.2 (GND2)
PB0: IC1.12 (PB0(ICP))
PB1: IC1.13 (PB1(OC1A))
PB2: IC1.14 (PB2(SS/OC1B)), JP8.4, MICRO-SD.PIN2
PB3: IC1.15 (PB3(MOSI/OC2)), JP8.3, MICRO-SD.PIN3
PB4: IC1.16 (PB4(MISO)), JP8.2, MICRO-SD.PIN7
PB5: IC1.17 (PB5(SCK)), JP8.1, MICRO-SD.PIN5
PC0: IC1.23 (PC0(ADC0)), T1.3 (OUT)
PC1: IC1.24 (PC1(ADC1)), JP5.2
PC2: IC1.25 (PC2(ADC2))
PC3: IC1.26 (PC3(ADC3)), R1.2, R2.2
PC4: *RTC.7 (SDA), IC1.27 (PC4(ADC4/SDA)), JP8.5
PC5: *RTC.8 (SCL), IC1.28 (PC5(ADC5/SCL)), JP8.6
PD0: IC1.30 (PD0(RXD)), JP5.4
PD1: IC1.31 (PD1(TXD)), JP5.5
PD2: IC1.32 (PD2(INT0)), JP6.2
PD3: IC1.1 (PD3(INT1)), JP6.3
PD4: IC1.2 (PD4(XCK/T0)), JP6.4
PD5: IC1.9 (PD5(T1)), JP6.5
PD6: IC1.10 (PD6(AIN0)), JP6.6
PD7: IC1.11 (PD7(AIN1)), JP2.1, JP8.7
Q1: C2.2, IC1.8 (PB7(XTAL2/TOSC2)), Q1.1
Q2: C1.2, IC1.7 (PB6(XTAL1/TOSC1)), Q1.3 (2)
RST: IC1.29 (PC6(/RESET)), JP5.6
VBAT: *RTC.6 (BAT), PAD1.1, PAD2.1
VCC: *RTC.2 (VCC), C4.2, C6.1, C7.2, C8.1, C9.2, IC1.4 (VCC), IC1.6 (VCC), IC1.18 (AVCC), JP1.2, JP5.3, MICRO-SD.PIN4, R1.1, T1.4 (VCC2), T1.5 (VCC)

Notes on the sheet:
Chris Kelley / AWQUA

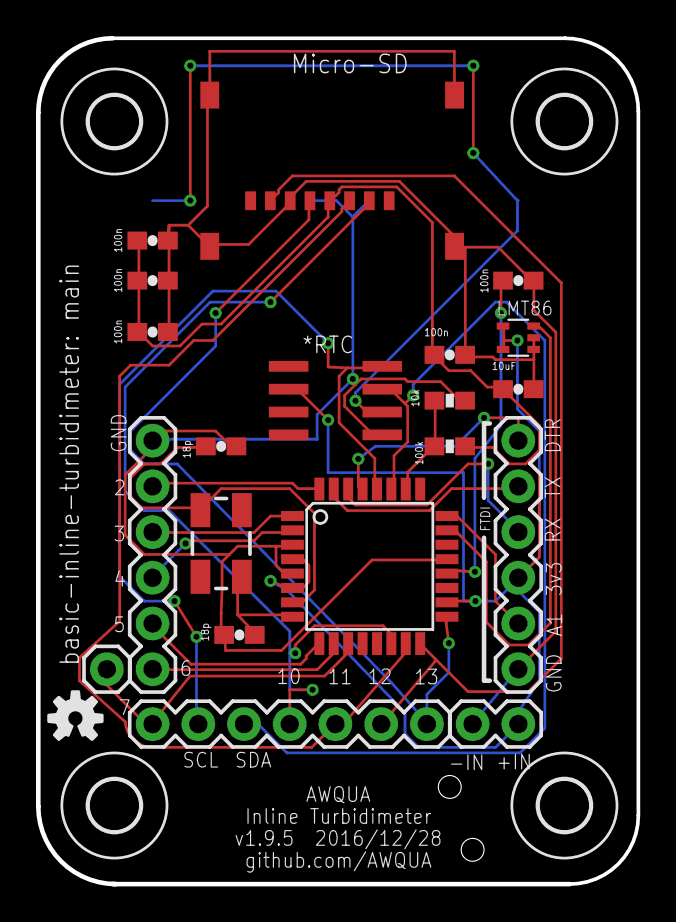
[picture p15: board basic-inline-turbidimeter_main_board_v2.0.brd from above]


Board: 2 copper layers, 33.3 x 47.0 mm, 31 parts (5 on the bottom side), 24 nets.

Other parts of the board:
U$1, U$3, U$5, U$6: 2,8
U$2, U$8: OSHW-LOGO-S

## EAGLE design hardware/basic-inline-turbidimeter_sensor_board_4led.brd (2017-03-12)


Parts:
C2: 100n; 0805
D1, D2, D3, D4: AL5809; SOD123
FRAME1: FRAME-LETTER; CREATIVE_COMMONS
HS1: M06SIP; 1X06
JP2: M01PTH; 1X01
JP5, JP6: M03PTH; 1X03
LED1, LED2, LED3, LED4: LED5MM
S1: TSL230RDSMD; TSL230RD

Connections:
GND_2: C2.1, HS1.GND (6), JP5.1, LED1.K (C), LED2.K (C), LED3.K (C), LED4.K (C), S1.GND, S1.S3
LED1: D1.C, LED3.A
LED2: D2.C, LED4.A
unnamed: D4.C, LED1.A
unnamed: D3.C, LED2.A
PC1_2: HS1.CTS (5), S1.OE
PD2_2: JP5.2, S1.OUT
PD3_2: D3.A, JP5.3
PD4_2: D4.A, JP6.1
PD5_2: D1.A, JP6.2
PD6_2: D2.A, JP6.3
PD7_2: JP2.1, S1.S1
VCC_2: C2.2, HS1.VCC (4), S1.S0, S1.S2, S1.VDD

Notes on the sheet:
Chris Kelley



Board: 2 copper layers, 44.5 x 20.3 mm, 16 parts (10 on the bottom side), 13 nets.

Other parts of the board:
U$5: OSHW-LOGO-S

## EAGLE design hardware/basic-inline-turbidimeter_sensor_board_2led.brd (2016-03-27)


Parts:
C1, C2: 100n; 0805
D1, D2, D5, D6: AL5809; SOD123
JP1, JP3: M06SIP; 1X06
JP2, JP4, JP5, JP6: M03PTH; 1X03
LED1, LED2, LED3, LED4: LED5MM
R1, R2, R3, R4: 220R; 0603-RES
U$1, U$3: TSL230RDSMD; TSL230RD

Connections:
GND: C1.1, JP2.1, JP3.GND (6), LED1.K (C), LED2.K (C), U$1.GND, U$1.S3
GND_2: C2.1, JP1.GND (6), JP5.1, LED3.K (C), LED4.K (C), U$3.GND, U$3.S3
LED1: D1.C, R4.1
LED2: D2.C, R3.1
unnamed: LED1.A, R1.2
unnamed: LED4.A, R3.2
unnamed: LED2.A, R2.2
unnamed: LED3.A, R4.2
unnamed: D6.C, R1.1
unnamed: D5.C, R2.1
PC1: JP3.CTS (5), U$1.OE
PC1_2: JP1.CTS (5), U$3.OE
PD2: JP2.2, U$1.OUT
PD2_2: JP5.2, U$3.OUT
PD3: JP2.3, U$1.S0
PD3_2: JP5.3, U$3.S0
PD4: JP4.1, U$1.S1
PD4_2: JP6.1, U$3.S1
PD5: D5.A, JP4.2
PD5_2: D1.A, JP6.2
PD6: D6.A, JP4.3
PD6_2: D2.A, JP6.3
VCC: C1.2, JP3.VCC (4), U$1.S2, U$1.VDD
VCC_2: C2.2, JP1.VCC (4), U$3.S2, U$3.VDD



Board: 2 copper layers, 44.5 x 38.1 mm, 24 parts (14 on the bottom side), 24 nets.

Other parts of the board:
U$2, U$5: OSHW-LOGO-S

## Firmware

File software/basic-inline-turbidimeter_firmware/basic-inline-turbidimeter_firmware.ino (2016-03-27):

//#define NO_PORTD_PINCHANGES
//#define NO_PORTC_PINCHANGES
//#include <GSM.h>

#include <avr/interrupt.h>
#include <avr/power.h>
#include <avr/sleep.h>
#include <JeeLib.h>
#include <PinChangeInt.h>
#include <SPI.h>
#include <SD.h>
#include <Wire.h>

#define RUN_CHECK_GND A2
#define RUN_CHECK_VCC  9
#define SLEEP_INDICATOR_OFF_TIME 29000
#define SLEEP_INDICATOR_ON_TIME  1000
#define SLEEP_INDICATOR_LOG_ERROR_ON_TIME  1000
#define SLEEP_INDICATOR_LOG_ERROR_OFF_TIME  5000

#define BAUD_RATE 19200
#define SD_CS   10
#define LED1     5
#define LED2     6

#define READ_TM  200 // milleseconds between frequency calculations
#define DOWN_TIME  20000

#define TSL_OE   A1    // frequency signal from the sensor
#define TSL_S1    3    // S1 and S0 are pins on the TSL230R chip
#define TSL_S0    2
#define TSL_FREQ  4    // frequency signal from the sensor
#define TPIN     A0
#define VPIN     A3
//#define TSL_S3       // frequency signal from the sensor
//#define TSL_S2       // frequency signal from the sensor

#define DIV_R1 10000   // resistance for R1
#define DIV_R2  1000   // resistance for R2

#define SERIAL_DEBUG true
#define RTC_DEBUG false
#define DEBUG_CHECK_CARD_AT_STARTUP true

File myFile;
boolean logfile_error = false;
unsigned long timer, loop_timer, pulse_count;
int scale = 2;
byte byt;
long idx = 0;
float system_voltage = 0.0;
//Sd2Card card;
//SdVolume volume;
//SdFile root;

ISR(WDT_vect) { Sleepy::watchdogEvent(); }  // boilerplate for low-power waiting

void setup() { 
  pinMode(RUN_CHECK_GND, OUTPUT);
  digitalWrite(RUN_CHECK_GND, LOW);
  pinMode(RUN_CHECK_VCC, OUTPUT);
  digitalWrite(RUN_CHECK_VCC, LOW);

  pinMode(TPIN, INPUT);  
  pinMode(LED1, OUTPUT);
  pinMode(LED2, OUTPUT);
  pinMode(TSL_FREQ, INPUT); // light sensor
  pinMode(TSL_S0, OUTPUT);  // light sensor
  pinMode(TSL_S1, OUTPUT);  // light sensor
//  pinMode(TSL_S2, OUTPUT);  // light source
//  pinMode(TSL_S3, OUTPUT);  // light source
  pinMode(TSL_OE, OUTPUT);  // light source
//  digitalWrite(TSL_S2, HIGH);
//  digitalWrite(TSL_S3, HIGH);  
  digitalWrite(TSL_OE, LOW); 
  digitalWrite(TSL_S0, HIGH);
  digitalWrite(TSL_S1, HIGH);

  Wire.begin();  
  Serial.begin(BAUD_RATE);
  Serial.println("starting...");
  Serial.end();
  
  // clear /EOSC bit // Sometimes necessary to ensure that the clock  // keeps running on just battery power. Once set, it shouldn't need to be reset but it's a good  // idea to make sure.
  Wire.beginTransmission(0x68); // address DS3231
  Wire.write(0x0E); // select register
  Wire.write(0b00011100); // write register bitmap, bit 7 is /EOSC
  Wire.endTransmission();  
  if(RTC_DEBUG){ set_rtc_time(byte(00), byte(8), byte(15), byte(6), byte(17), byte(4), byte(15)); delay(100);}
  char out_ts[30];
  get_rtc_time(out_ts);
  //Serial.print("timestamp: ");
  //Serial.println(out_ts);
    
  pinMode(SD_CS, OUTPUT);
  //setup_sd();
  Serial.begin(BAUD_RATE);
  if (!SD.begin(SD_CS)) {Serial.println("initialization failed!");}
  else{Serial.println("initialization done.");}
  // re-open the file for reading:
  myFile = SD.open("log.txt");
  if (myFile){
    if(DEBUG_CHECK_CARD_AT_STARTUP) {
      Serial.println("log.txt:");
      while (myFile.available()) {
        //Serial.write(
        myFile.read();
      }
      myFile.close();
    }
  }else{
    Serial.println("error opening log.txt");
    logfile_error = true;
  }
  myFile.close();
  //PCintPort::attachInterrupt(TSL_FREQ, add_pulse, RISING);
}

void add_pulse() {pulse_count++;}

void loop(){
  loop_timer = millis();
  Serial.print("loop begins as...");
  Serial.println(millis());
  char rd_idx[15];
  char out_ts[30];
  char out_data[10];
  get_rtc_time(out_ts);
  sprintf (rd_idx, "%lu", idx);
  take_readings(6, false, false);
  float reading = take_readings(8, true, false);
  //char tmp[10];
  dtostrf(reading,3,3,out_data);
  myFile = SD.open("log.txt", FILE_WRITE);
  if (myFile) {
    float t = read_temperature();
    float v = getVoltageLevel();
    Serial.begin(BAUD_RATE);
    Serial.print("writing to logfile\t");
    Serial.print(t);
    Serial.print(",");
    Serial.print(v);
    Serial.print(",");
    Serial.print(millis());//out_ts);
    Serial.print(",");
    Serial.println(out_data);
    myFile.print(rd_idx);
    myFile.print(",");
    myFile.print(t);
    myFile.print(",");
    myFile.print(v);
    myFile.print(",");
    myFile.print(millis());//out_ts);
    myFile.print(",");
    myFile.println(out_data);
    myFile.close();
    logfile_error = false;
  } else {
    logfile_error = true;
  }
  idx++;

  Serial.println("preparing to sleep now...");
  delay(100);
  digitalWrite(TSL_OE, HIGH);
  
  //long quiet_time = DOWN_TIME - SLEEP_INDICATOR_OFF_TIME - SLEEP_INDICATOR_ON_TIME;
  //Serial.print("time elapsed...");
  //Serial.println(millis() - loop_timer);
  //Serial.print("msec to delay:");
  //Serial.println((DOWN_TIME - millis() + loop_timer) % (SLEEP_INDICATOR_OFF_TIME + SLEEP_INDICATOR_ON_TIME));
  //Serial.println((quiet_time - millis() + timer) % (SLEEP_INDICATOR_OFF_TIME + SLEEP_INDICATOR_ON_TIME));
  //replace with delay(quiet_time % (SLEEP_INDICATOR_OFF_TIME + SLEEP_INDICATOR_ON_TIME)) to bring (SLEEP_INDICATOR_OFF_TIME + SLEEP_INDICATOR_ON_TIME) to an even divisor of quiet_time
  //then replace the while loop with an (quiet_time / (SLEEP_INDICATOR_OFF_TIME + SLEEP_INDICATOR_ON_TIME)) for loop

  //Serial.end();
  boolean modder = true;
  while(millis() - loop_timer < DOWN_TIME){
    if(modder){
      Serial.print("sleep for ");
      Serial.println((DOWN_TIME - millis() + loop_timer) % (SLEEP_INDICATOR_OFF_TIME + SLEEP_INDICATOR_ON_TIME));
      delay(100);
      Sleepy::loseSomeTime((DOWN_TIME - millis() + loop_timer) % (SLEEP_INDICATOR_OFF_TIME + SLEEP_INDICATOR_ON_TIME));
      modder = false;
    }else{
      if(logfile_error){
        for(int i = 0; i < 3; i++){
          Sleepy::loseSomeTime(SLEEP_INDICATOR_LOG_ERROR_ON_TIME);
          digitalWrite(9, HIGH);
          Sleepy::loseSomeTime(SLEEP_INDICATOR_LOG_ERROR_OFF_TIME);
          digitalWrite(9, LOW);
        }
      }else{
        Serial.print("sleep for ");
        Serial.println(SLEEP_INDICATOR_OFF_TIME + SLEEP_INDICATOR_ON_TIME);
        delay(100);
        Sleepy::loseSomeTime(SLEEP_INDICATOR_OFF_TIME + SLEEP_INDICATOR_ON_TIME);
        //digitalWrite(9, HIGH);
        //Sleepy::loseSomeTime(SLEEP_INDICATOR_ON_TIME);
        //digitalWrite(9, LOW);
      }
    }
  }

  //Serial.begin(BAUD_RATE);
  delay(100);
  Serial.print("waking up now at...");
  Serial.println(millis());
  digitalWrite(TSL_OE, LOW);
}

/****************************************************************************************************/
float getVoltageLevel(){
  analogReference(INTERNAL);
  delay(10);
  float vpin = analogRead(VPIN); //drop the first reading
  delay(100);
  vpin = float(analogRead(VPIN));
  if(SERIAL_DEBUG){
    Serial.print("raw voltage divider value: ");
  }
  float divider_value = float(DIV_R2) / float(DIV_R1+DIV_R2);
  system_voltage = vpin/ 1023.0 * 1.1 / divider_value;  
  return system_voltage;
}

float read_temperature(){
  //with 10mV per degree C, and 1100mV for 1024 steps, scaling_factor = 10/(1100/1024) ~ 9.3
  //10.9mV/C, 1024 steps from
  analogReference(DEFAULT);
  delay(5);
  int t = analogRead(TPIN);
  analogReference(INTERNAL);
  delay(5);
  return float(t);
}

float take_readings(int rdgs, boolean printout, boolean dark_counts){
  PCintPort::attachInterrupt(TSL_FREQ, add_pulse, RISING);  delay(5);
  float rd = 0.0, high = 0.0, low = 1000000.0, sum = 0.0, avg = 0.0;
  for(int i = 0; i < rdgs; ++i){
    rd = 0.0;
    if(dark_counts){
      digitalWrite(LED1, LOW);
      digitalWrite(LED2, LOW);
      delay(2);
      timer = millis();
      pulse_count = 0;
      while (timer + READ_TM > millis()){;}
      rd -= pulse_count / scale;
    }
    digitalWrite(LED1, HIGH);
    digitalWrite(LED2, HIGH);
    delay(2);
    timer = millis();
    pulse_count = 0;
    while (timer + READ_TM > millis()){;}
    rd += pulse_count / scale;
    if(rd > high){ high = rd;}
    if(rd < low){low = rd;}
    sum += rd;
    if(printout && SERIAL_DEBUG){
      Serial.print("reading: ");
      Serial.println(rd);
    }
  }
  digitalWrite(LED1, LOW);
  digitalWrite(LED2, LOW);
  avg = 0.0;
  if(rdgs > 2){
    sum -= high + low;
    avg = sum / (rdgs - 2);
  }else{
    avg = sum / rdgs;
  }
  detachInterrupt(TSL_FREQ);
  delay(5);
  /*if(printout && SERIAL_DEBUG){
    Serial.print("average: ");
    Serial.println(avg);
    Serial.println();
    delay(100);
  }*/
  return avg;
}

void get_rtc_time(char *buffer){
  // send request to receive data starting at register 0
  Wire.beginTransmission(0x68); // 0x68 is DS3231 device address
  Wire.write((byte)0); // start at register 0
  Wire.endTransmission();
  Wire.requestFrom(0x68, 7); // request info
  while(Wire.available())  { 
    int seconds = Wire.read(); // get seconds
    int minutes = Wire.read(); // get minutes
    int hours = bcdToDec(Wire.read() & 0b111111);//Wire.read();   // get hours
    int dotw = bcdToDec(Wire.read());
    int dotm = bcdToDec(Wire.read());
    int mnth = bcdToDec(Wire.read());
    int yr = bcdToDec(Wire.read());
    //hours = //(((hours & 0b00100000)>>5)*20 + ((hours & 0b00010000)>>4)*10 + (hours & 0b00001111)); // convert BCD to decimal (assume 24 hour mode)
    seconds = (((seconds & 0b11110000)>>4)*10 + (seconds & 0b00001111)); // convert BCD to decimal
    minutes = (((minutes & 0b11110000)>>4)*10 + (minutes & 0b00001111)); // convert BCD to decimal
    yr += 2000;
    
    if(seconds >= 10 && minutes >= 10){sprintf(buffer, "%d/%d/%d %d:%d:%d", yr, mnth, dotm, hours, minutes, seconds);}
    if(seconds >= 10 && minutes < 10){sprintf(buffer, "%d/%d/%d %d:0%d:%d", yr, mnth, dotm, hours, minutes, seconds);}
    if(seconds < 10 && minutes < 10){sprintf(buffer, "%d/%d/%d %d:0%d:0%d", yr, mnth, dotm, hours, minutes, seconds);}
    if(seconds < 10 && minutes >= 10){sprintf(buffer, "%d/%d/%d %d:%d:0%d", yr, mnth, dotm, hours, minutes, seconds);}
    //s += 2000 + yr;    s += "/" + mnth;     s += "/" + dotm;    s += " " + hours;     s += ":" + minutes;     s += ":" + seconds;
  }
}

//set the time on the DS3231M
void set_rtc_time(byte seconds, byte minutes, byte hours, byte dotw, byte dotm, byte mnth, byte yr){  // sets time and date data to DS3231
  Wire.beginTransmission(0x68);
  Wire.write(0); // set next input to start at the seconds register
  Wire.write(decToBcd(seconds)); // set seconds
  Wire.write(decToBcd(minutes)); // set minutes
  Wire.write(decToBcd(hours)); // set hours
  Wire.write(decToBcd(dotm)); // set day of week (1=Sunday, 7=Saturday)
  Wire.write(decToBcd(dotm)); // set date (1 to 31)
  Wire.write(decToBcd(mnth)); // set month
  Wire.write(decToBcd(yr)); // set year (0 to 99)
  Wire.endTransmission(); 
}

// Convert binary coded decimal to normal decimal numbers
byte bcdToDec(byte val)  {return ( (val/16*10) + (val%16) );}

//opposite of bcdToDec
byte decToBcd(byte val){return( (val/10*16) + (val%10) );}

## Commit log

2016-03-27 migrating from AWQUA/Measurement until polished
    [basic-inline-turbidimeter_analysis.20151021.xlsx, basic-inline-turbidimeter_main_board.brd, basic-inline-turbidimeter_main_board.sch, basic-inline-turbidimeter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]
2017-01-16 hardware updates
    [basic-inline-turbidimeter_main_board_v1.9.brd, basic-inline-turbidimeter_main_board_v1.9.sch, basic-inline-turbidimeter_main_board_v2.0.brd, basic-inline-turbi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]
2017-03-12 minor updates
    [basic-inline-turbidimeter_main_board_v2.0.brd, basic-inline-turbidimeter_main_board_v2.0.csv, basic-inline-turbidimeter_main_board_v2.0.sch, basic-inline-turbi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]
2017-03-17 adding solder paste mask for v2.1
    [basic-inline-turbidimeter_main_board_v2.1.dxf]
2017-03-28 added svg fror acrylic window laser cutting

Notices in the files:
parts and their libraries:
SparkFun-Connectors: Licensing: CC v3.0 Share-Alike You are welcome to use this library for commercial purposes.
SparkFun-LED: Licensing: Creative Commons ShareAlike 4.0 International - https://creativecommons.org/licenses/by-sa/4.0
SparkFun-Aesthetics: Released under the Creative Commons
